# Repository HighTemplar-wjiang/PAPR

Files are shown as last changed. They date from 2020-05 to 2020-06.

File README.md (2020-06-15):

# PAPR (Powered Air-Purifying Respirator)
DIY PAPR for health workers [wiki](https://en.wikipedia.org/wiki/Powered_air-purifying_respirator). 

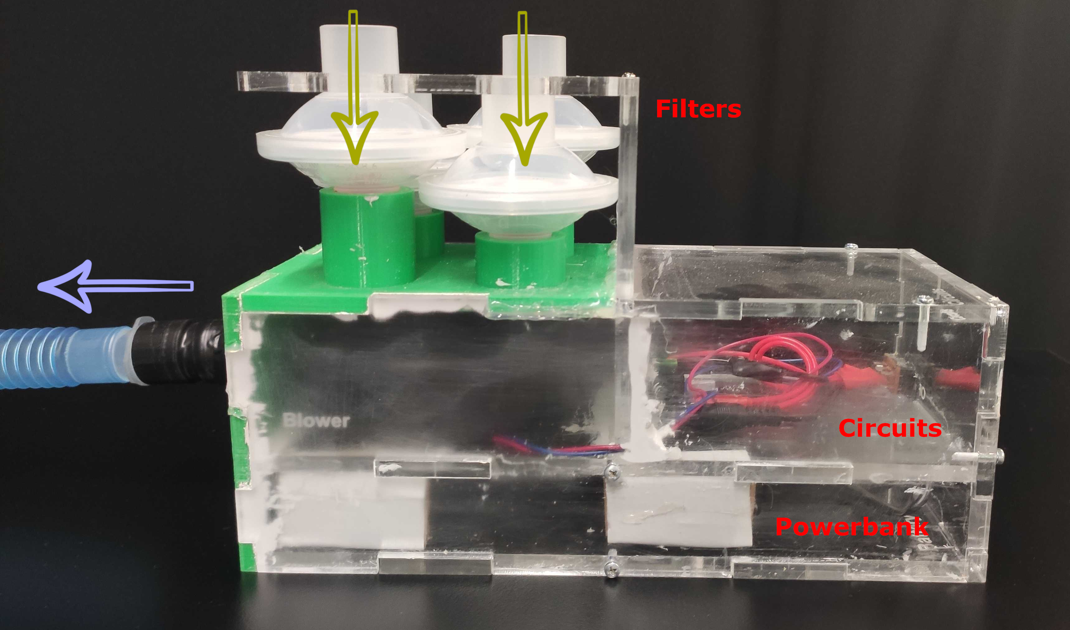
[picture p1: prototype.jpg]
prototype


## Update on 21st May.
- Uploaded source files, finalizing design and test.

## Update on 16th April.
- Battery test using a 20,000 mAh power bank -- 9 hours 4 minutes. 

## Update on 15th April. 
- Now using a 20,000 mAh [power bank](https://www.jaycar.com.au/20-000mah-power-bank-with-dual-type-a-quick-charge-and-type-c-power-delivery-usb-ports/p/MB3797) that is smaller, cheaper and easier to get. 
- Testing enclosure using 6mm Acrylic + 3D print fan blower adapter. 

## Update on 13th April.
- Tested a 12.8V 7.5Ah [lithum battery](https://www.jaycar.com.au/12-8v-7-5ah-lithium-deep-cycle-battery/p/SB2201), the fan worked for 15 hours, with less than 25% volume left.
- Tested an all 3D print enclosure, the cost was ~300 AUD. Changed to 3D print + laser cutting scheme. 

## Update on 11th April.
- Tested PC fan (1200 RPM), the static pressure was not sufficient. Probably a high speed fan is required.
- Changed design to [blower fan](https://www.jaycar.com.au/97mm-x-94mm-12v-dc-blower-fan-ball-bearing-2-wire/p/YX2532) which has higher static pressure. 

## Specifications ([ref](https://www.3m.com.au/3M/en_AU/company-au/all-3m-products/~/3M-Jupiter-PAPR-Helmet-JTM-406C/?N=5002385+8711017+3293696209&rt=rud))
- **Battery life**: > 8 hours (preferred 10 hours or longer)
- **Capacity per Minute (Metric)**: 150 to 230 litres per min (2.5 - 3.8 L/sec or 5.3 - 8.12 CFM)
- **Resistance to flow (N95 filter)**: 
  - 0.56 cmH<sub>2</sub>O @1L/sec, 0.74 cmH<sub>2</sub>O @5L/sec, <1.50 cmH<sub>2</sub>O @ 14L/sec.
  - or 55 Pa @1L/sec, 73 Pa @5L/sec, < 147 Pa @14 L/sec.
  
## Materials
- **[Blower fan](https://www.jaycar.com.au/97mm-x-94mm-12v-dc-blower-fan-ball-bearing-2-wire/p/YX2532)**
  - Air volume: 0.74 m<sup>2</sup>/min (26.13 CFM).
  - Static pressure: 1.0 inchH<sub>2</sub>O (2.54 cmH<sub>2</sub>O or 248.84 Pa).
  - Power consumption: 12 V x 0.86 A = 10.32 Watts (12.4 V x 0.38 A = 4.712 Watts as measured).
  - 3D-printed adapter [[in progress]()]. 
- **[Power bank](https://www.jaycar.com.au/20-000mah-power-bank-with-dual-type-a-quick-charge-and-type-c-power-delivery-usb-ports/p/MB3797)**
  - Capacity: 20000 mAh.
  - Voltage regulator: USB 12V step-up [power cable](https://www.jaycar.com.au/universal-usb-12v-step-up-power-cable/p/PP1978).
  - Slide [switch](https://www.jaycar.com.au/miniature-dpdt-panel-mount-switch/p/SS0821).
- **[CPAP/BiCAP bacteria filter](https://www.google.com/search?q=bacteria+filter&newwindow=1&rlz=1C1CHBF_en-GBAU878AU878&sxsrf=ALeKk00tQMjTFyXqZiyXmlXnysL8wDm1-g:1586943680106&tbm=isch&source=iu&ictx=1&fir=CWFMSYPq2Sse6M%253A%252Cul_TTRfInZ_iRM%252C_&vet=1&usg=AI4_-kTNiGZukLHlwl-E7zovhjH9Xxoe-Q&sa=X&ved=2ahUKEwjH9dLykeroAhV3wTgGHakdCnQQ9QEwBXoECAcQJw#imgrc=CWFMSYPq2Sse6M:)**
  - In-flow diameters: 22 mm inner, 26 mm outer.
  - Out-flow diameters: 19 mm inner, 22 mm outer. 
  - 3D-printed filter adapter [[in progress]()].
- Laser cutted pannels for enclosure
  - 6 mm Acrylic. 
  - M3 screws x 10.
  - Silicone glue. 
  - Silicone tape.

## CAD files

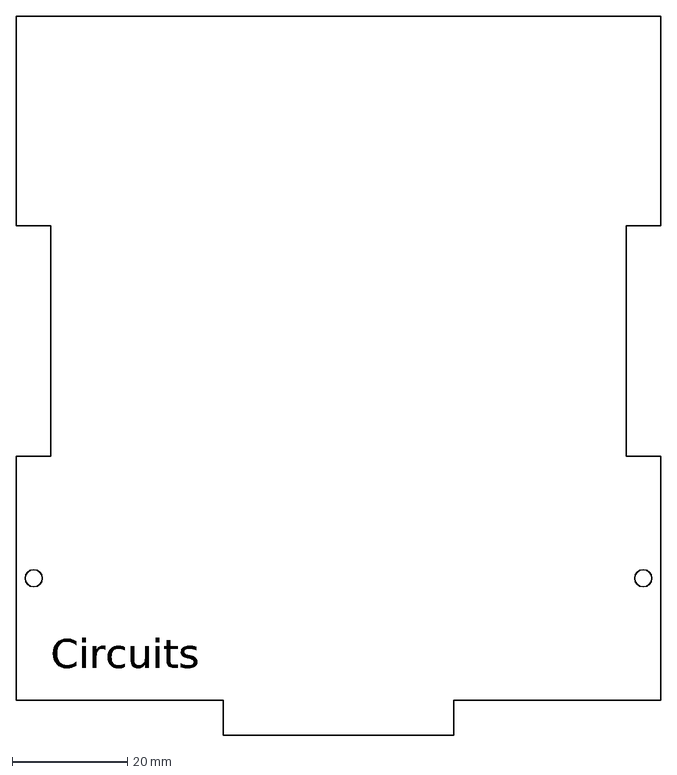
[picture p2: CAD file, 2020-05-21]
laser/dxf/PAPR_topback_panel.dxf
Circuits

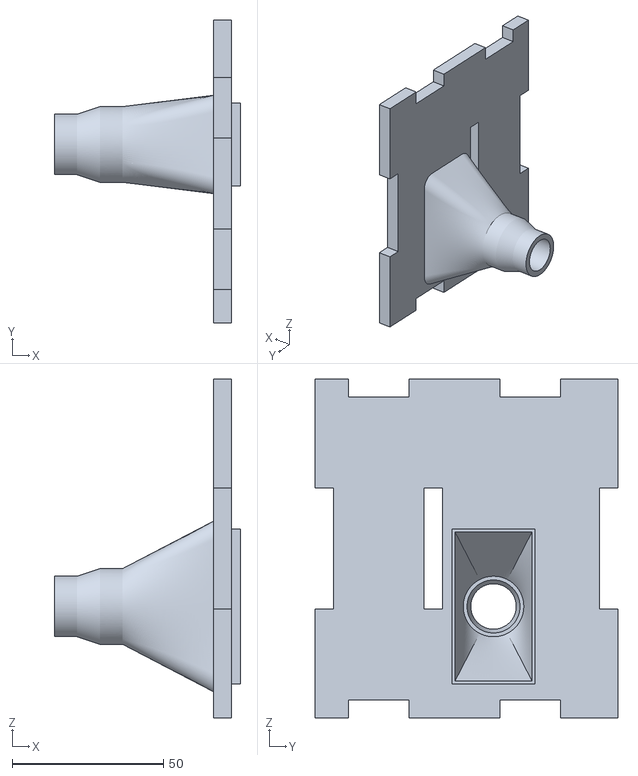
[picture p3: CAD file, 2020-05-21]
stl/Component_blower_adapter.stl
61.5 x 100.0 x 112.0

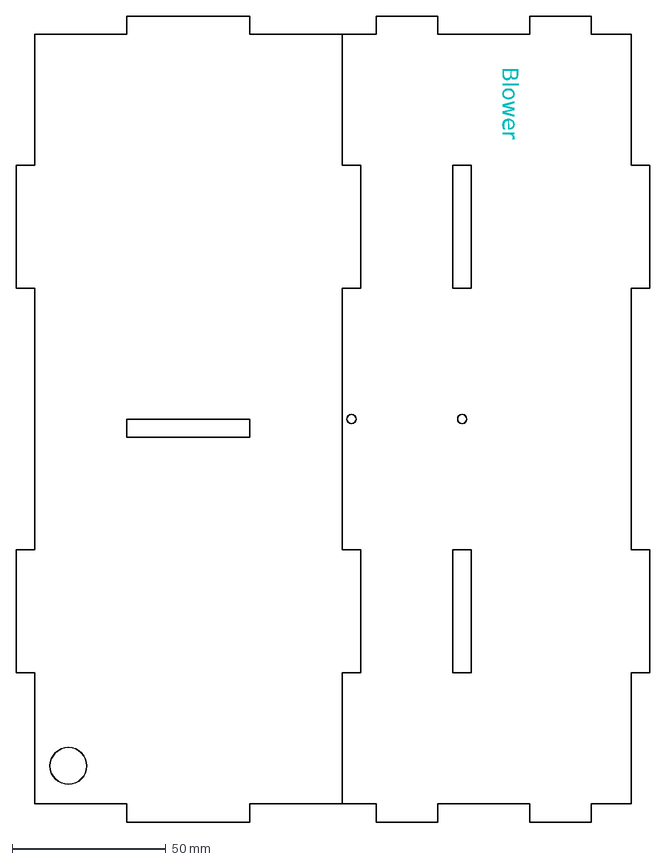
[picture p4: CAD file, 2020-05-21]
laser/dxf/PAPR_middle_panels.dxf
Blower

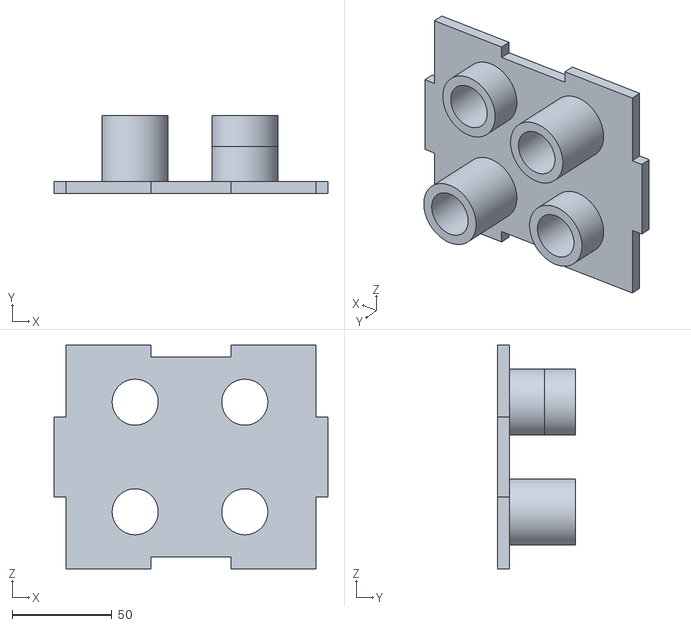
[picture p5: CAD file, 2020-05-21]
stl/Component_blower_top_panel.stl
137.0 x 39.0 x 112.0

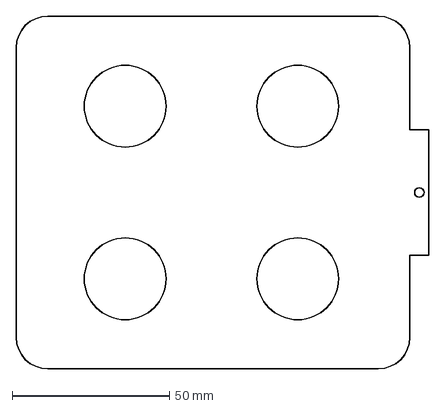
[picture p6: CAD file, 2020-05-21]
laser/dxf/PAPR_filter_locker.dxf
131.0 x 112.0 mm

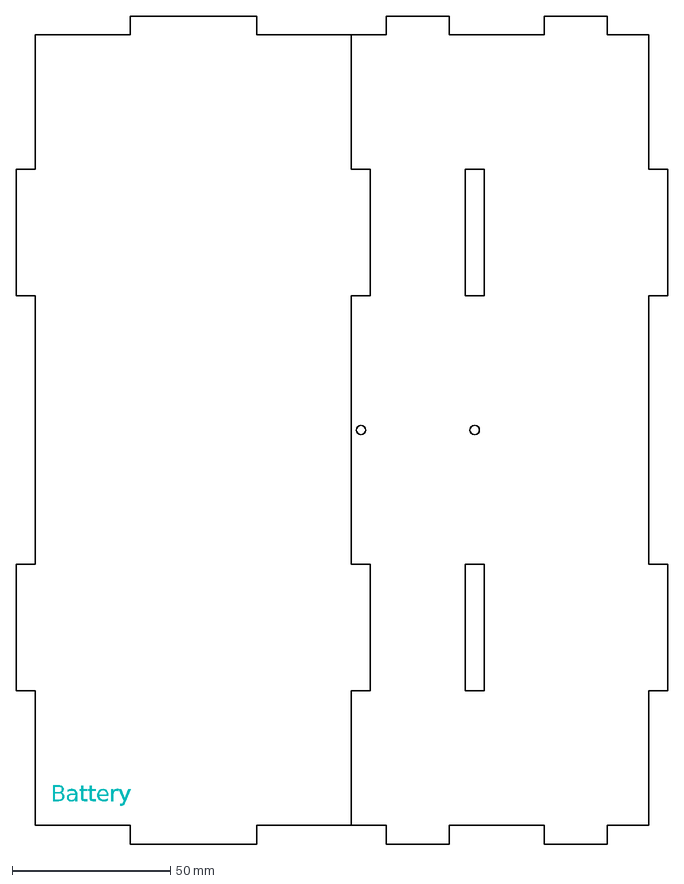
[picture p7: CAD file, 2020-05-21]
laser/dxf/PAPR_bottom_panels.dxf
Battery

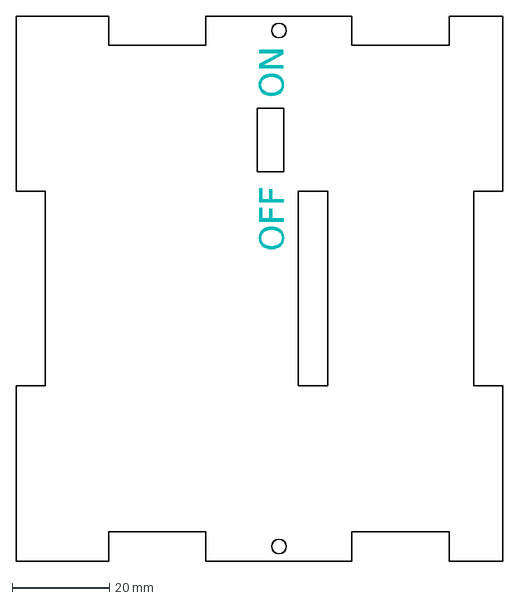
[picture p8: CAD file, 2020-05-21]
laser/dxf/PAPR_back_panel.dxf
OFF
ON

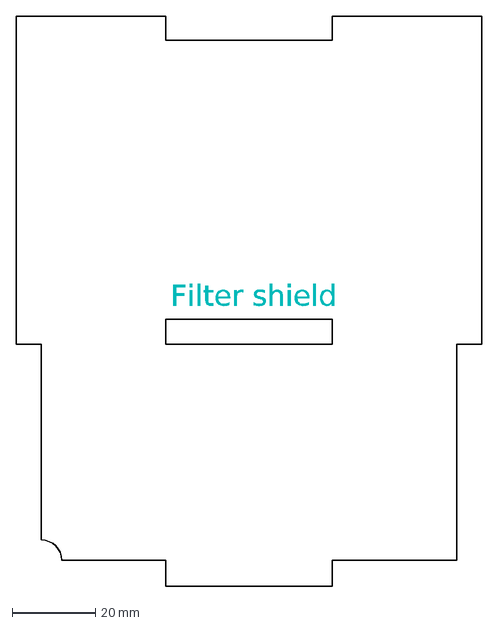
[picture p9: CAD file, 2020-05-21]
laser/dxf/PAPR_filter_shield.dxf
Filter shield

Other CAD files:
laser/PAPR_v1.3dm
stl/CPAP.f3d

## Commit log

2020-04-16 updated power bank time test
2020-05-21 uploaded source files
    [CPAP.f3d, Component_blower_adapter.stl, Component_blower_top_panel.stl, PAPR_back_panel.dxf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]
